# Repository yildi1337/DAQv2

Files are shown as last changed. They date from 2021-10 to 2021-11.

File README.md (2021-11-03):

# DAQv2
A Dual-Channel, 24-Bit, 256 kS/s Real-Time Hi-Speed USB 2.0 Data Acquisition (DAQ) Device based on STM32H7

# Details
The recording of analog measurement signals is often done with so-called data acquisition (DAQ) devices. Commercial devices from [National Instruments](http://www.ni.com) are commonly used, but unfortunately also very expensive. The goal of this project was to develop a first prototype of a low-cost DAQ device that can compete with commercial devices, i.e. both the hardware DAQ board as well as software for receiving and analyzing the data is necessary.

The basic structure of a DAQ is very simple. In principle, only an analog-to-digital converter (ADC) and an FPGA or microcontroller are needed in order to send the measurement data in real time to a computer. Here, the [AD7768-4 from Analog Devices](https://www.analog.com/en/products/ad7768-4.html) has been chosen, which offers up to 4 synchronous channels (but I only use 2 channels), a sampling rate of 256 kS/s and a resolution of 24 bit. Each sample consists of 3 data bytes and one status byte. So with the two channels used, the net data rate is 2 x 256 kS/s x 4 byte = 2.048 MByte/s = 16.384 MBit/s.

To keep the hardware cheap and the compatibility high, I decided to use a microcontroller (and not an FPGA) and a USB connection. Since the net data rate is higher than 12 MBit/s (USB Full-Speed), a USB Hi-Speed connection (up to 480 MBit/s) is required. However, most microcontrollers allow USB Hi-Speed connections only with an additional external PHY. Therefore, in my recent project [DAQv1](https://github.com/yildi1337/DAQv1), I have chosen a microcontroller from Microchip's PIC32MZ family, since they already have the Hi-Speed PHY integrated. Due to the poor documentation of the Microchip microcontrollers, I decided to use a microcontroller from the STM32H7 family again, which can be easily operated with an external PHY.

Technical summary of the developed platform:
* ADC: [AD7768-4BSTZ](https://www.analog.com/en/products/ad7768-4.html)
* Number of channels: 2
* Sample rate: 256 kS/s
* Resolution: 24 bit
* Reference voltage: 5 V
* Microcontroller: [STM32H753ZIT6](https://www.st.com/en/microcontrollers-microprocessors/stm32h753zi.html)
* USB 2.0 Hi-Speed (net data rate: 16.384 MBit/s)
* Preamlifier: 0-80 dB by means of two [AD8338ACPZ-R7](https://www.analog.com/en/products/ad8338.html)
* Programmable input coupling (AC with lower cutoff frequency of approx. 10 mHz and DC)
* Programmable input type (single ended and differential)
* LC Display for displaying input configuration
* Two buttons for chaning the input configuration
* Noise: See below

If you have any questions, feel free to contact me!

# Pictures

Not yet available.

# 3D Model

A 3D model of the PCB can be found in the Autodesk Fusion Cloud where it can be downloaded in various file types.

<p align="center">
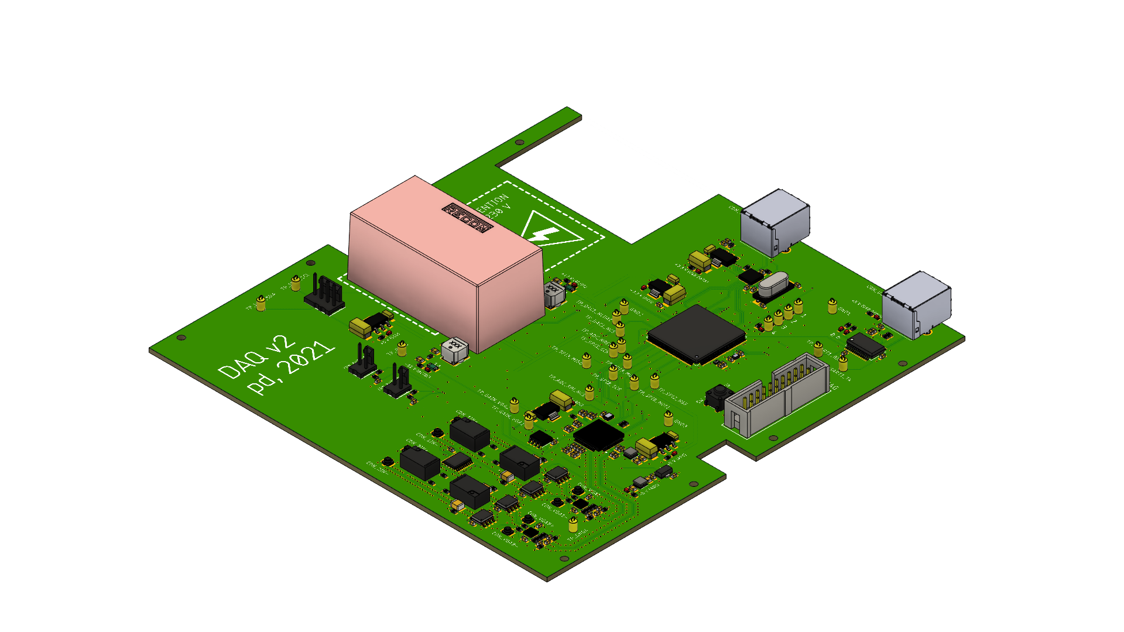
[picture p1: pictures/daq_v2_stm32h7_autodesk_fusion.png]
    
</p>

In addition, a step file of the complete device, i.e. a model of the PCB embedded into the housing ([TEKO 935.9](https://www.teko.it/de/produkte/produktfamilie/FP/serie/euro-93)), can be found in the directory *3d_model*.

<p align="center">
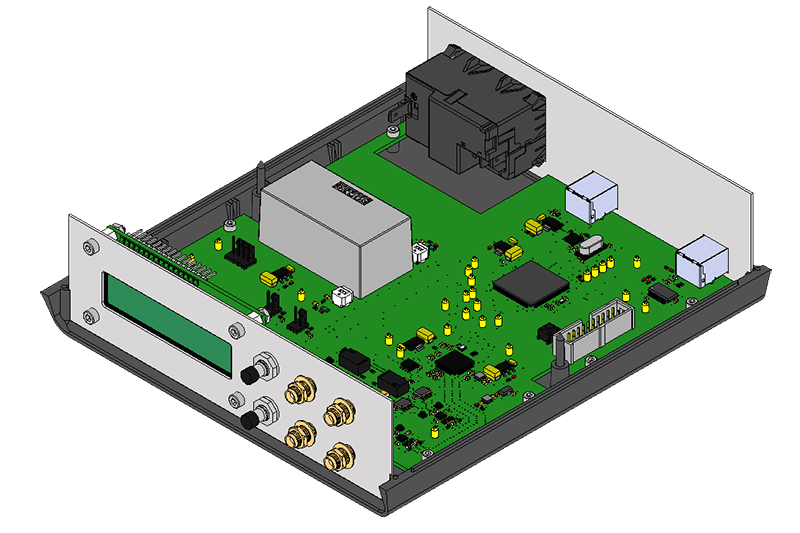
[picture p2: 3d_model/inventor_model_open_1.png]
  
</p>

<p align="center">
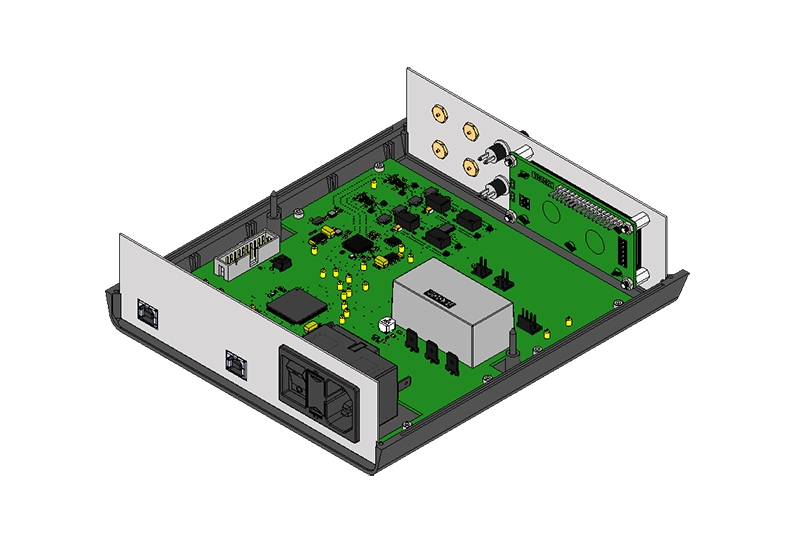
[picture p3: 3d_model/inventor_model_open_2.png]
  
</p>

<p align="center">
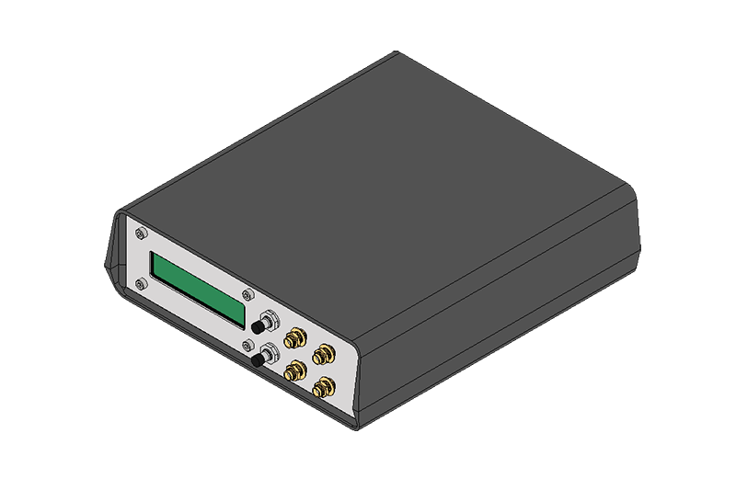
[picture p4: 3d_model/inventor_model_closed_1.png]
  
</p>

<p align="center">
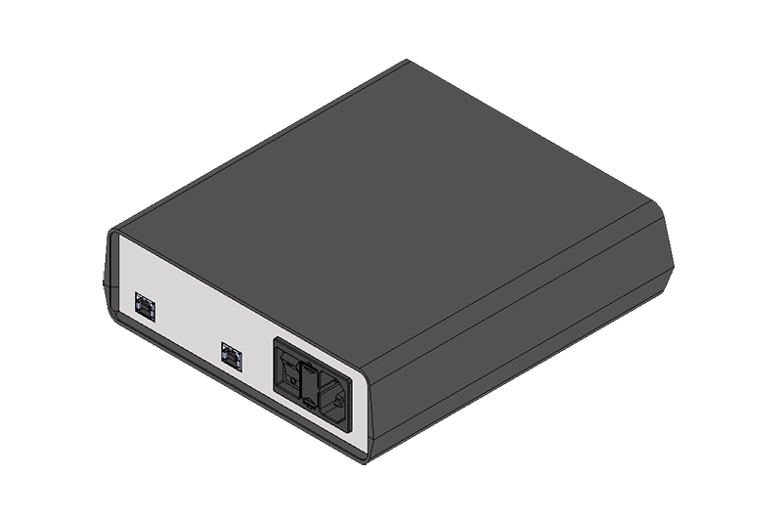
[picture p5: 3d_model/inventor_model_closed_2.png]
  
</p>

# Schematics
Please see subdirectory *schematics*.

# Board
The PCB was designed in Autodesk EAGLE 9.6.2 and manufactured by [JLCPCB](https://jlcpcb.com/). All Gerber files can be found in the subdirectory *gerber_files*.

<p align="center">
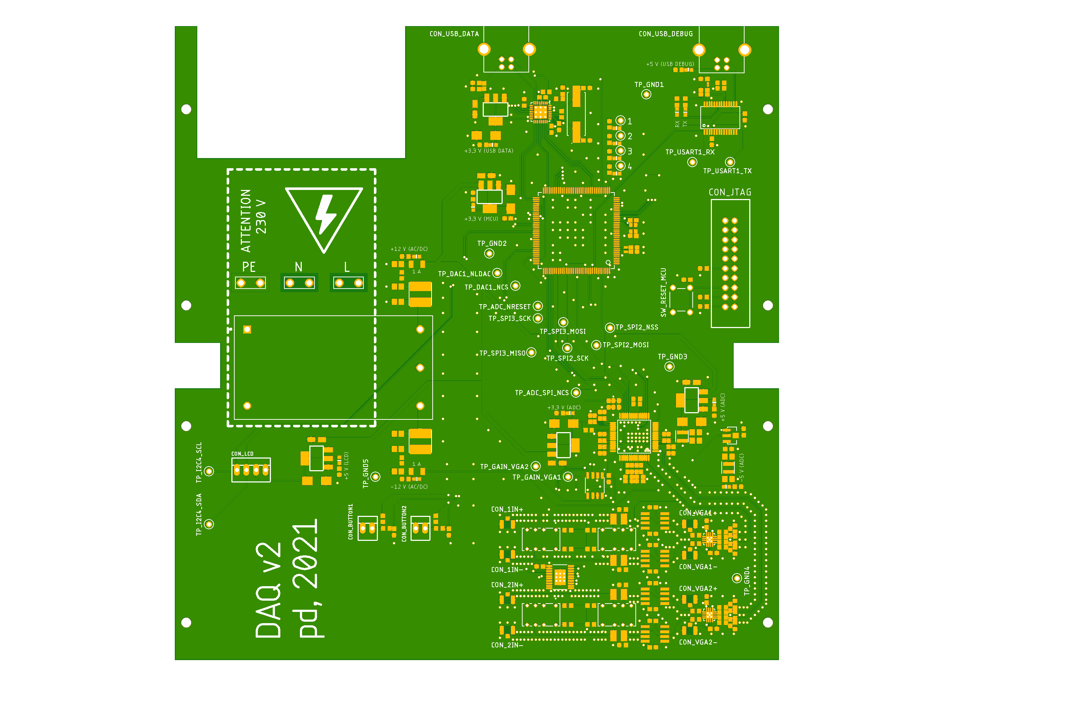
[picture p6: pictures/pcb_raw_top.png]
  
</p>

<p align="center">
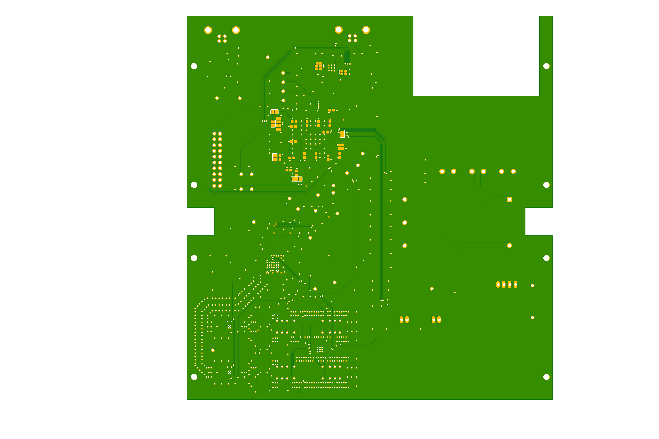
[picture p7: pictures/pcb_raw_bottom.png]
  
</p>

# Firmware
The source code of software running on the STM32H753ZIT6 can be found in the subdirectory *firmware*). For the development and debugging I used STM32CubeIDE version 1.7.0. For programming I used the ST-LINK/V2 in-circuit debugger/programmer.

# USB Debug Interface

A tool for the graphical display of status information and for controlling the DAQ v2 hardware via the virtual serial interface (second USB-B port) has been developed in Python, see subdirectory *debug_interface*.

<p align="center">
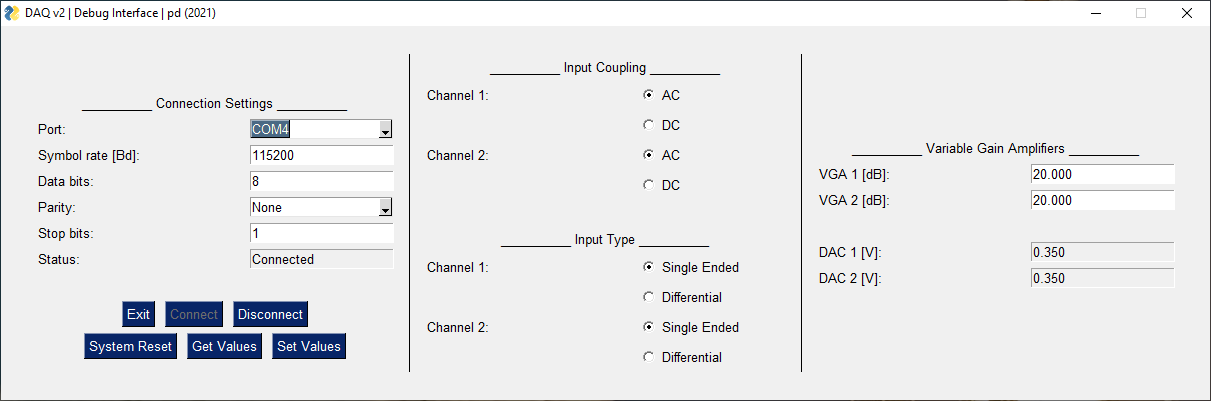
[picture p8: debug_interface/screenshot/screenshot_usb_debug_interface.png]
  
</p>

# LabVIEW Real-Time Data Receiver

A software vor real-time data reception and visualization of the signals both in time and frequency domain has been developed in LabVIEW, see subdirectory *labview*.

<p align="center">
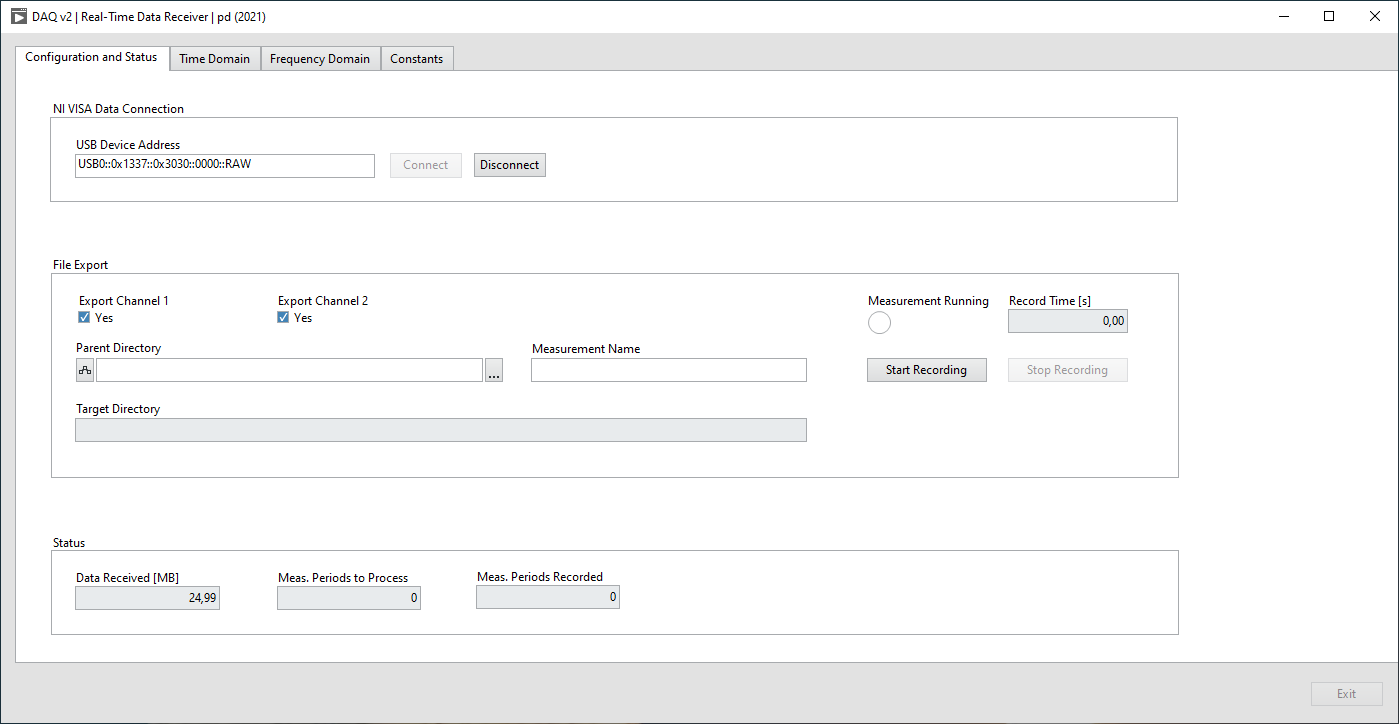
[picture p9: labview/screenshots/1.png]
  
</p>

<p align="center">
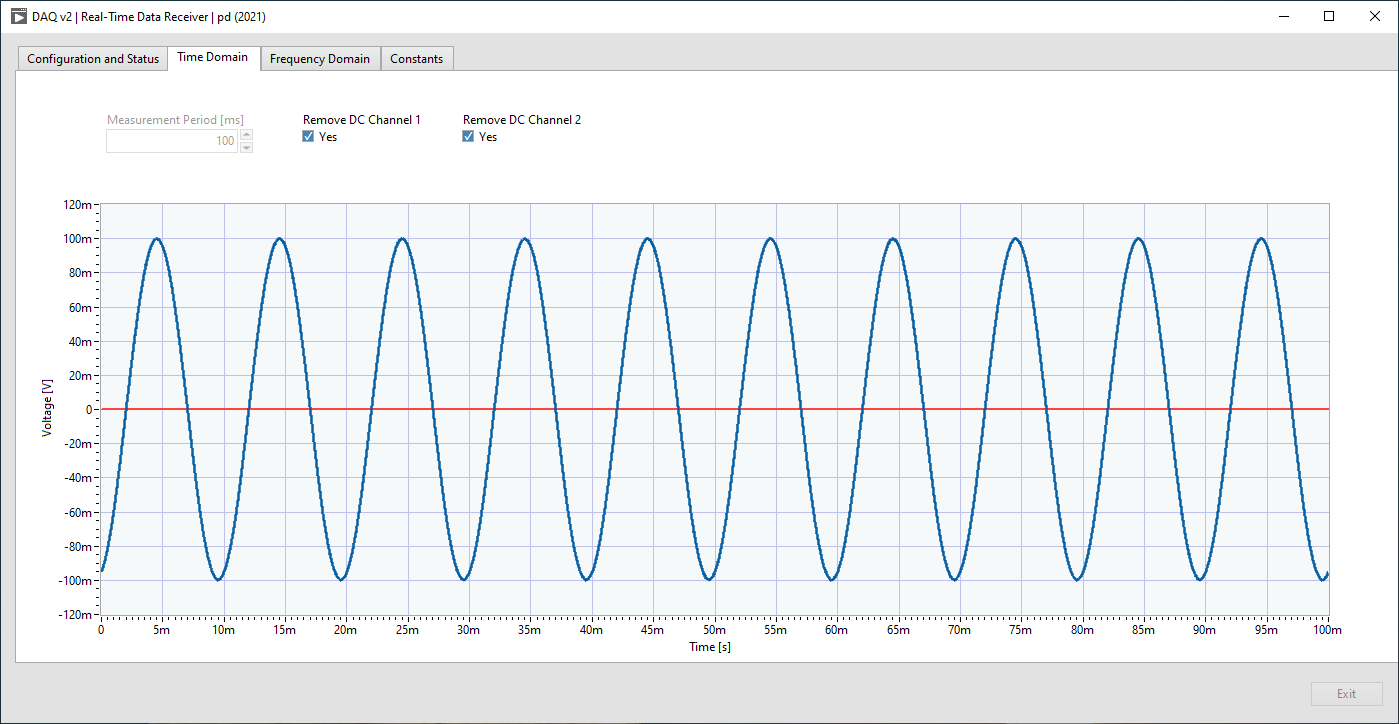
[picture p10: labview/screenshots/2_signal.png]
  
</p>

<p align="center">
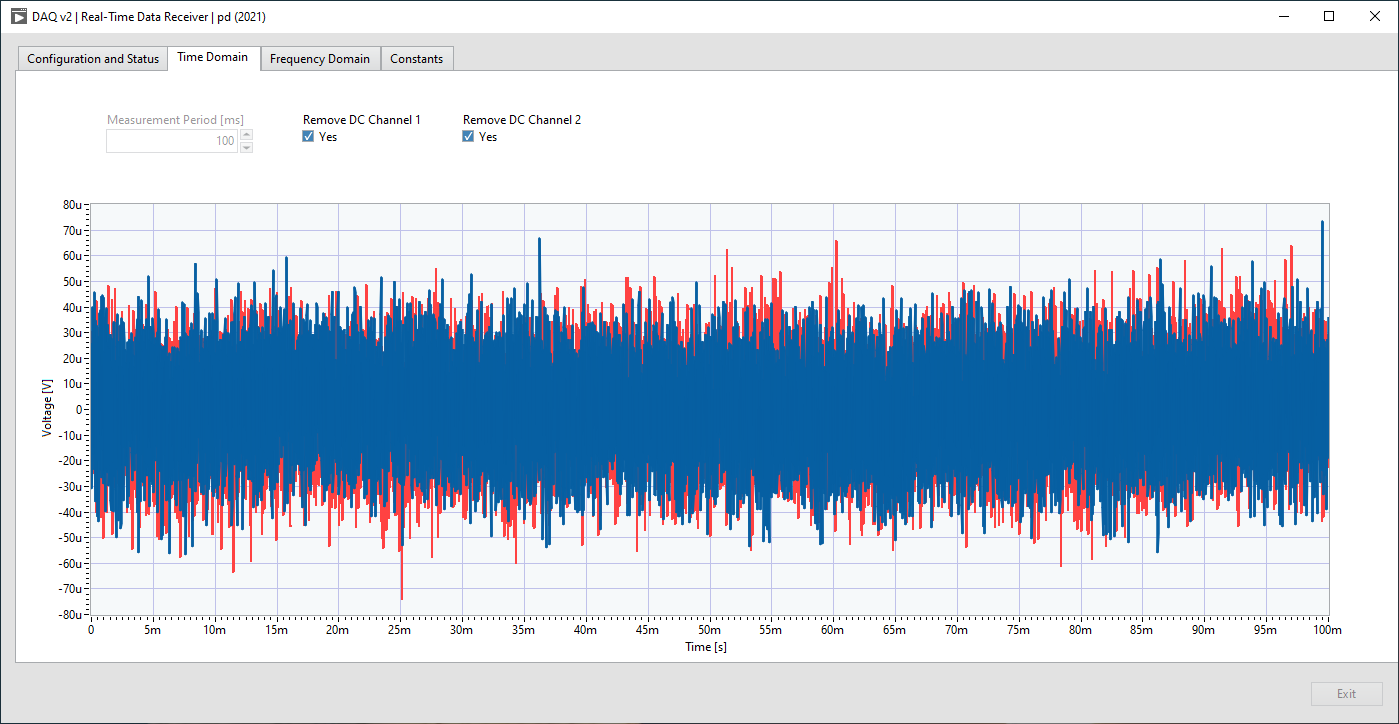
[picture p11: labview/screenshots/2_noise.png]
  
</p>

<p align="center">
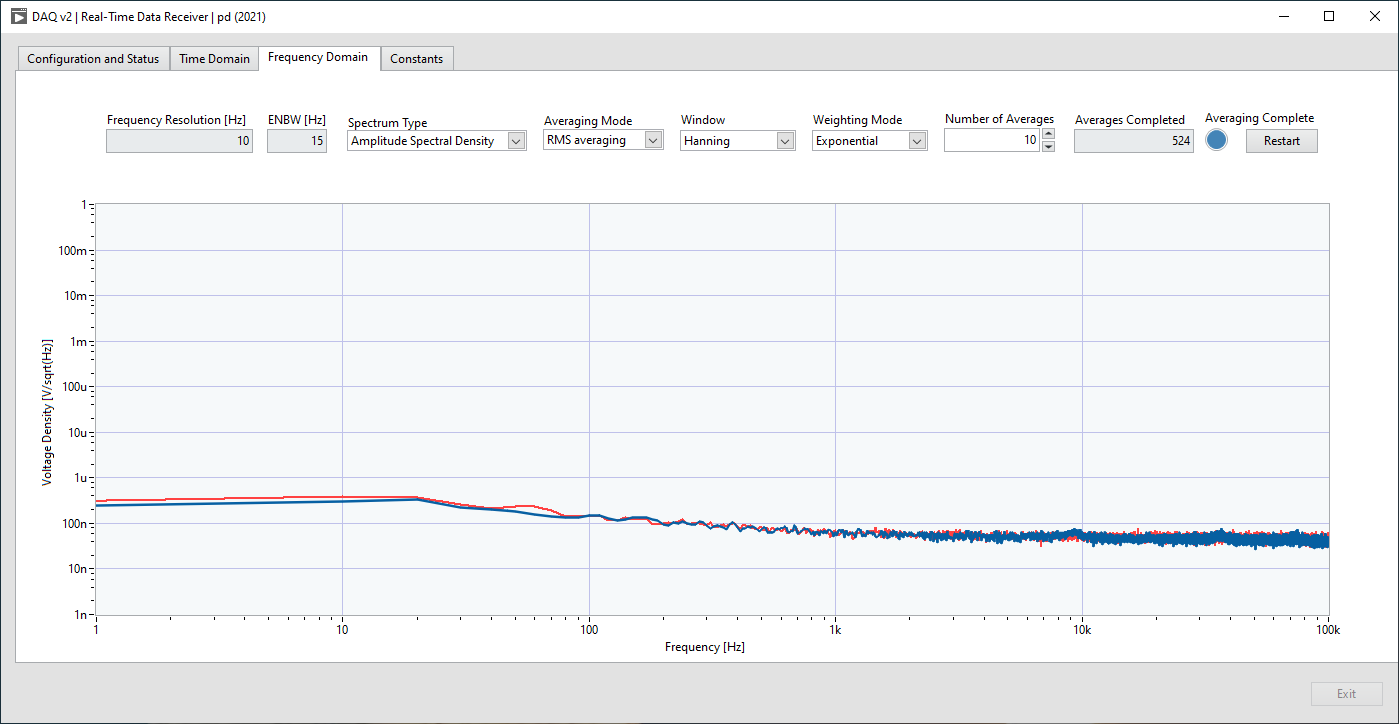
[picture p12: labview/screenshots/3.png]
  
</p>

<p align="center">
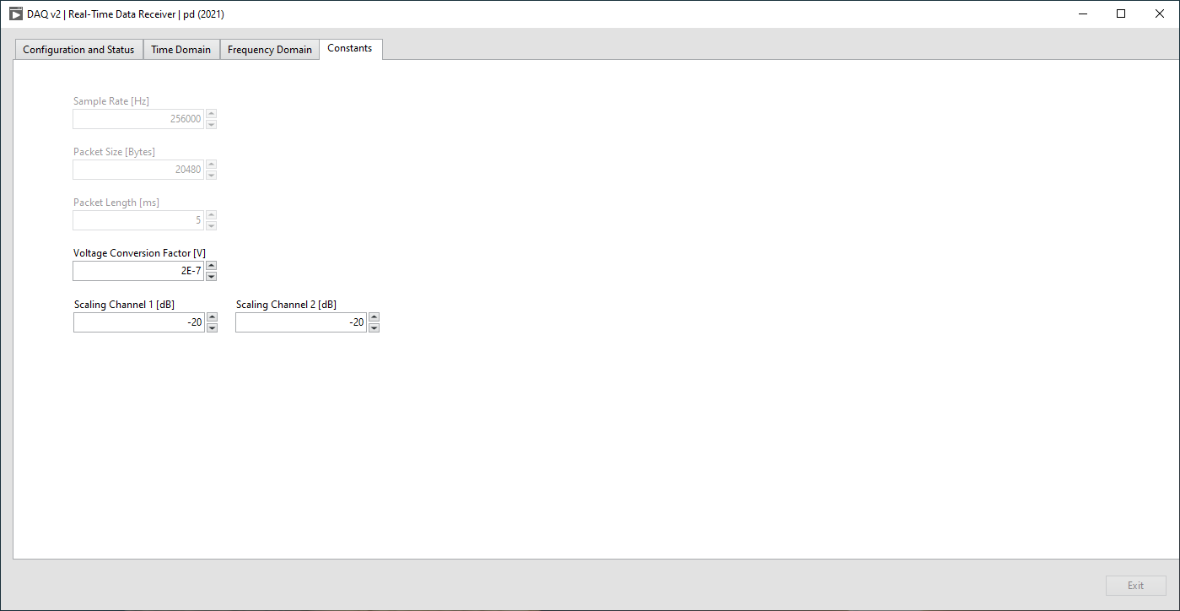
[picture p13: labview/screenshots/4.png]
  
</p>

# Noise

The voltage noise densities were measured for various cases (open inputs, shortened inputs, and 50 Ohm resistors connected to the inputs). 

Not yet available.

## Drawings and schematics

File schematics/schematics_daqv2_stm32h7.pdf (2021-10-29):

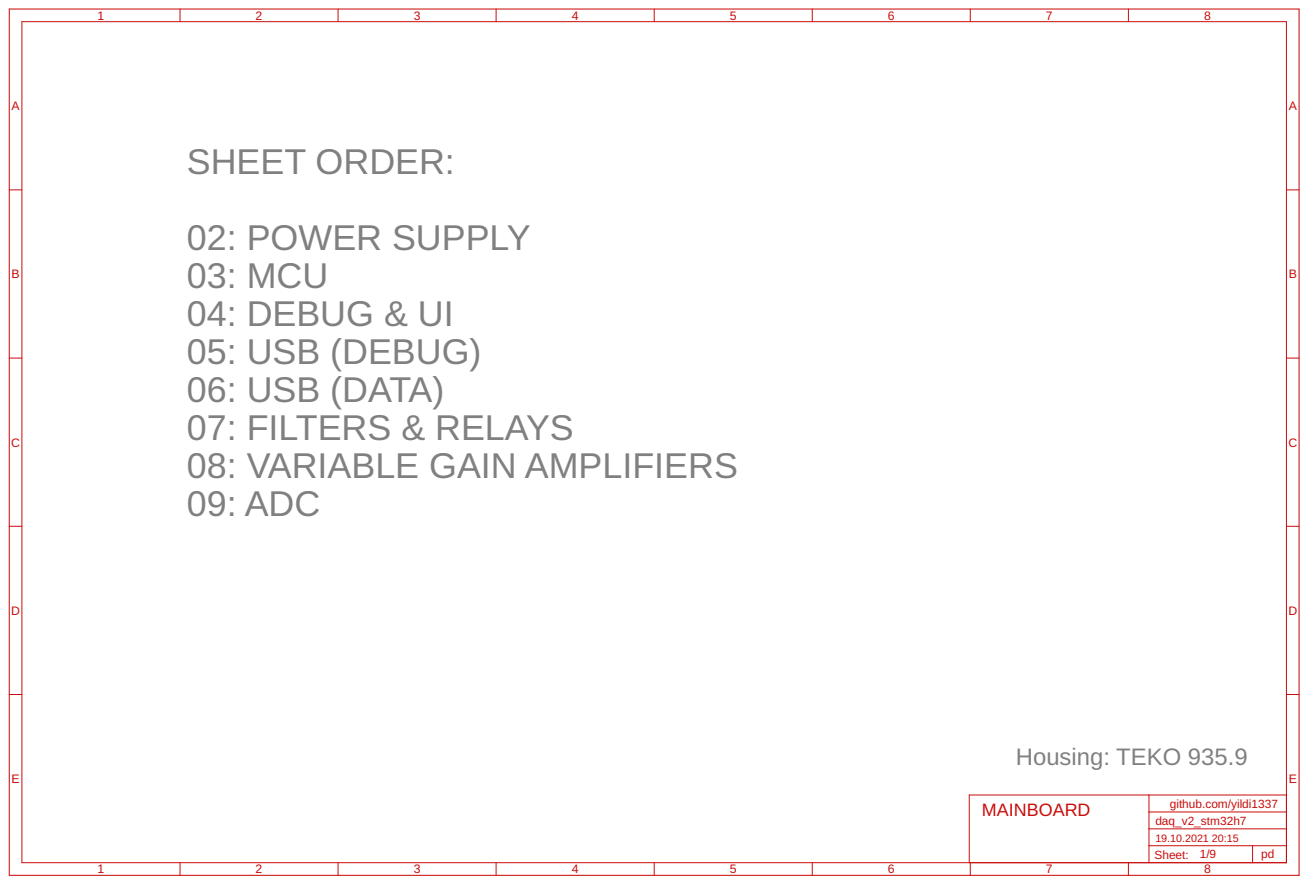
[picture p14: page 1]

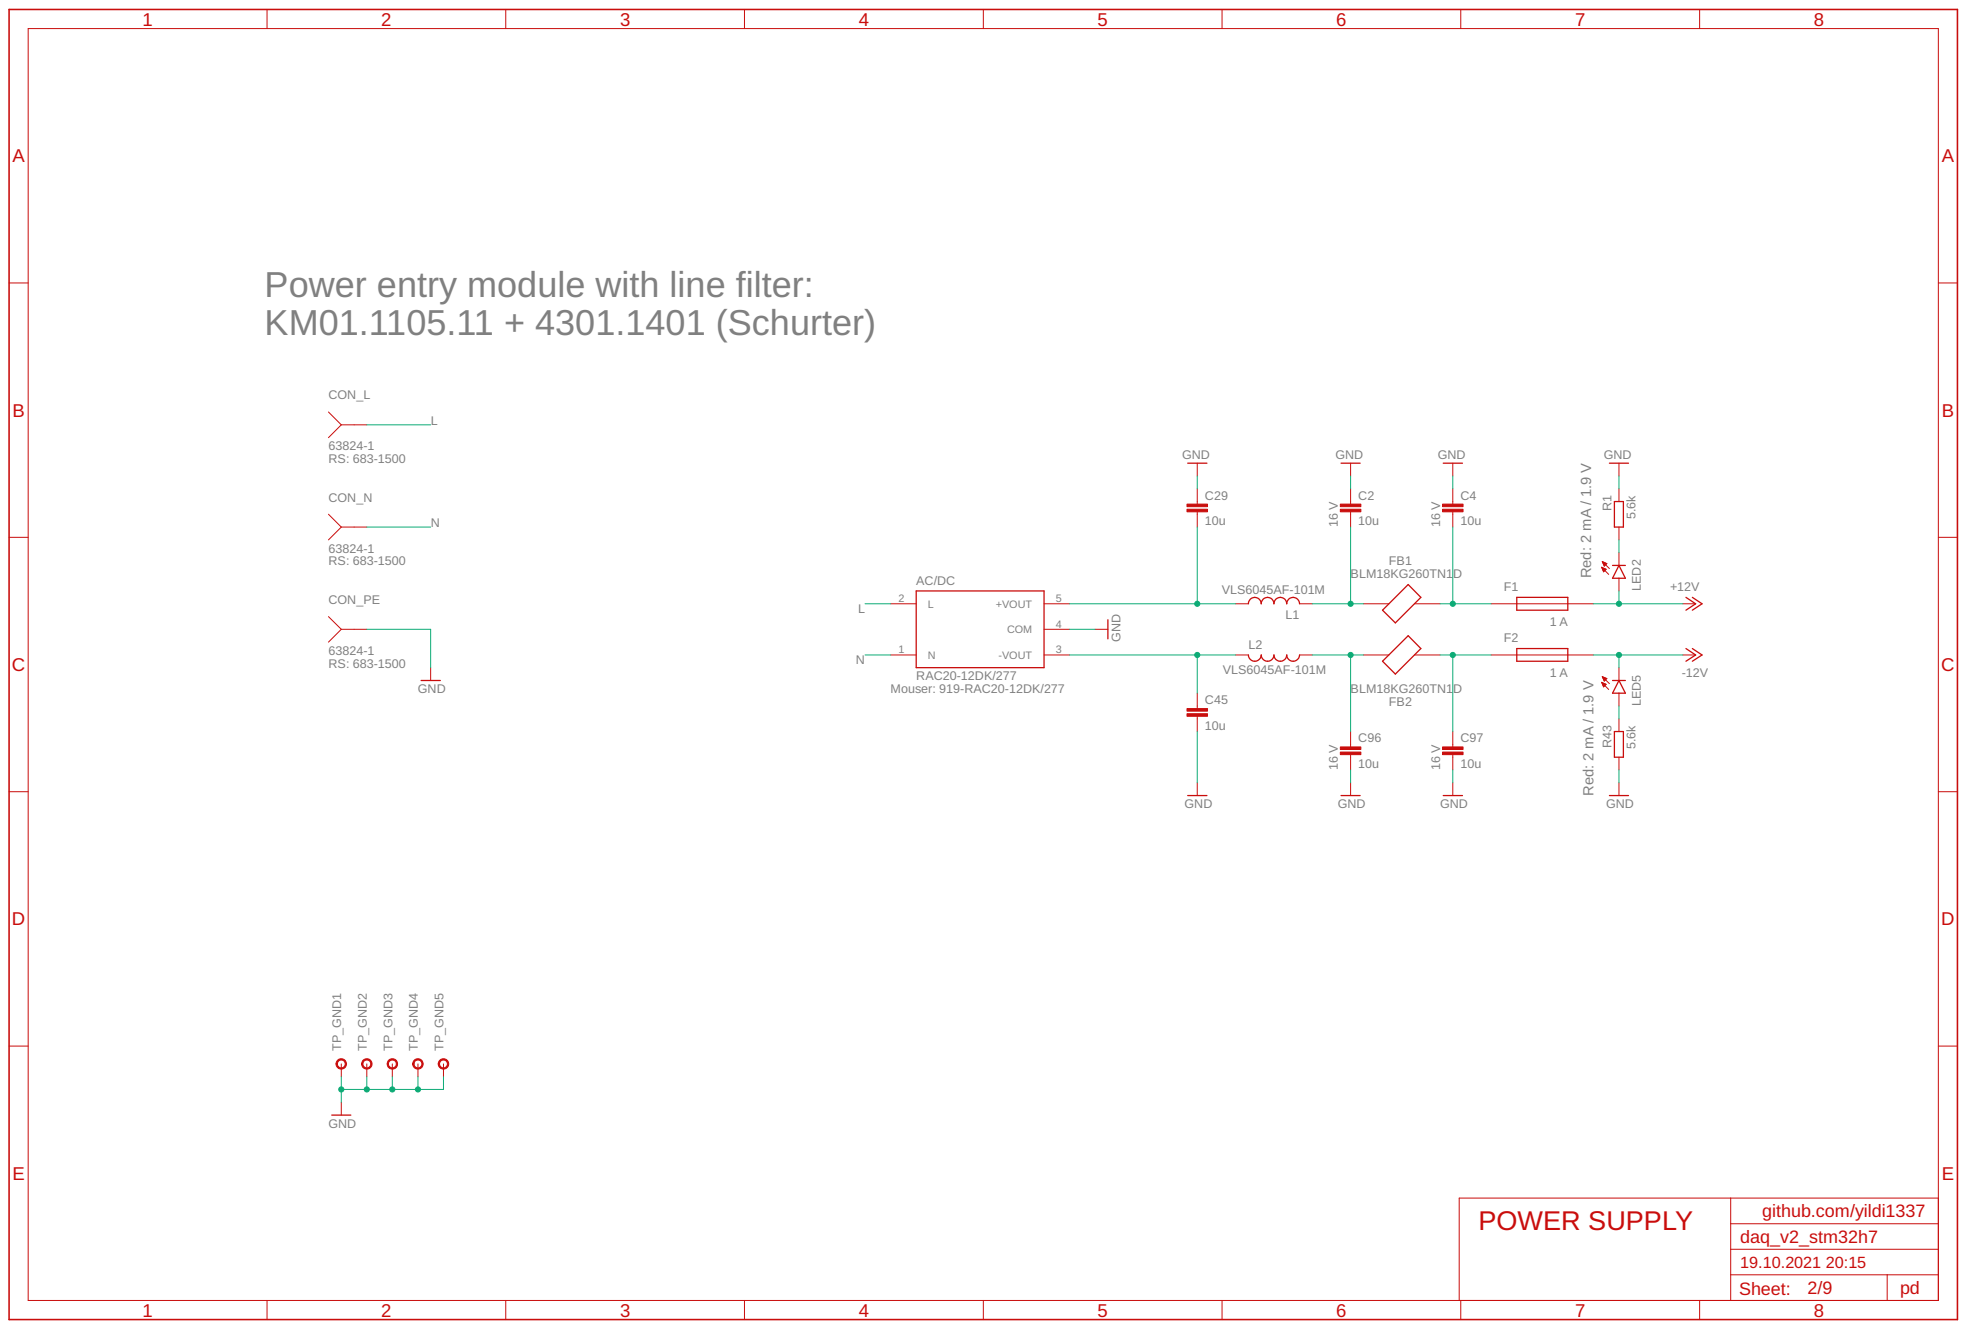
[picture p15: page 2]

Power entry module with line filter:
KM01.1105.11 + 4301.1401 (Schurter)

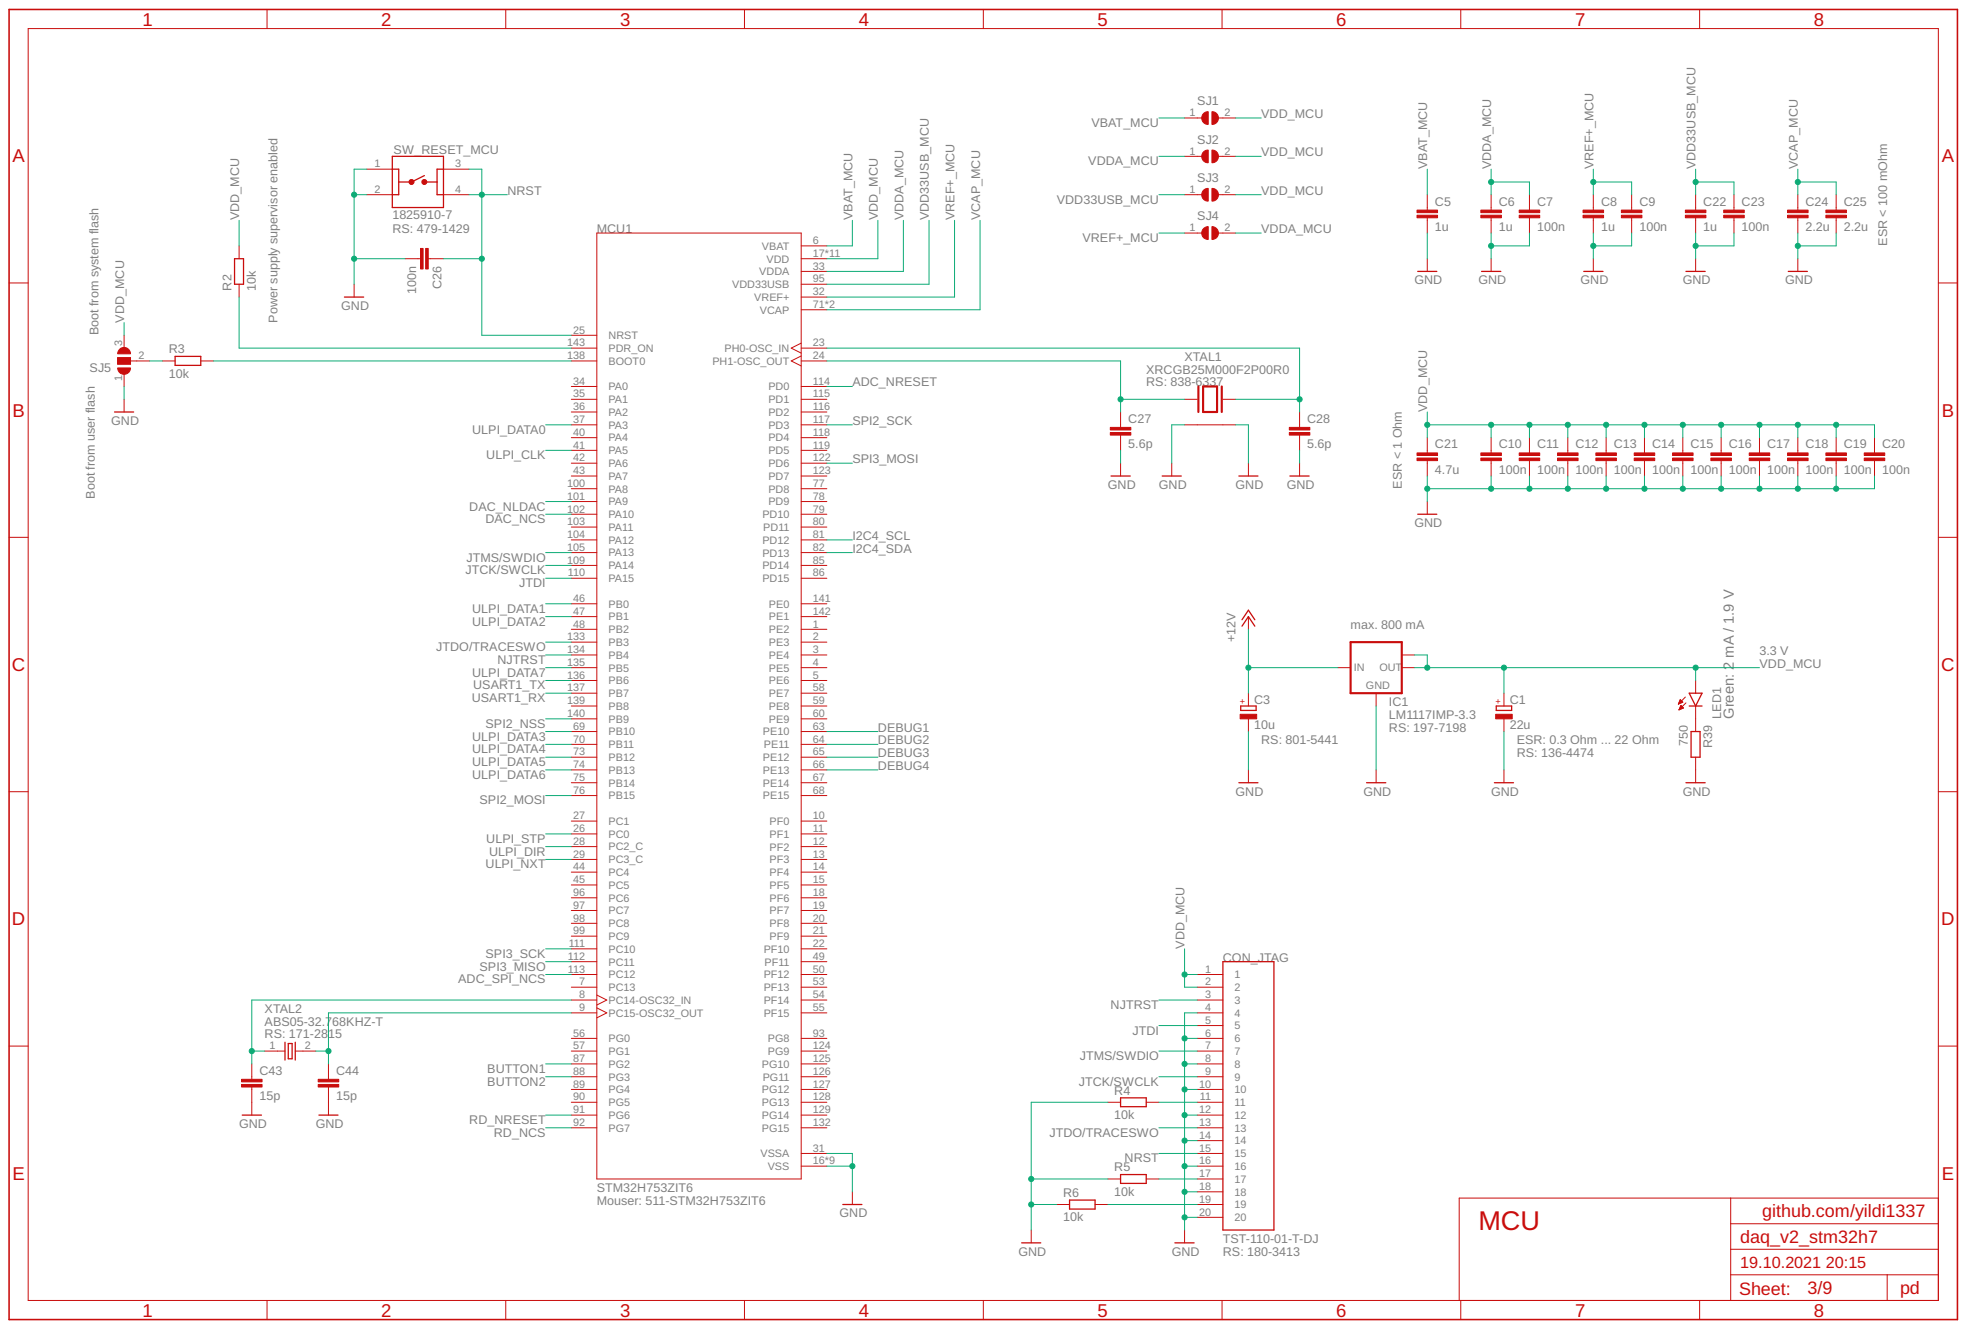
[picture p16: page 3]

Power supply supervisor enabled

Boot from user flash Boot from system flash

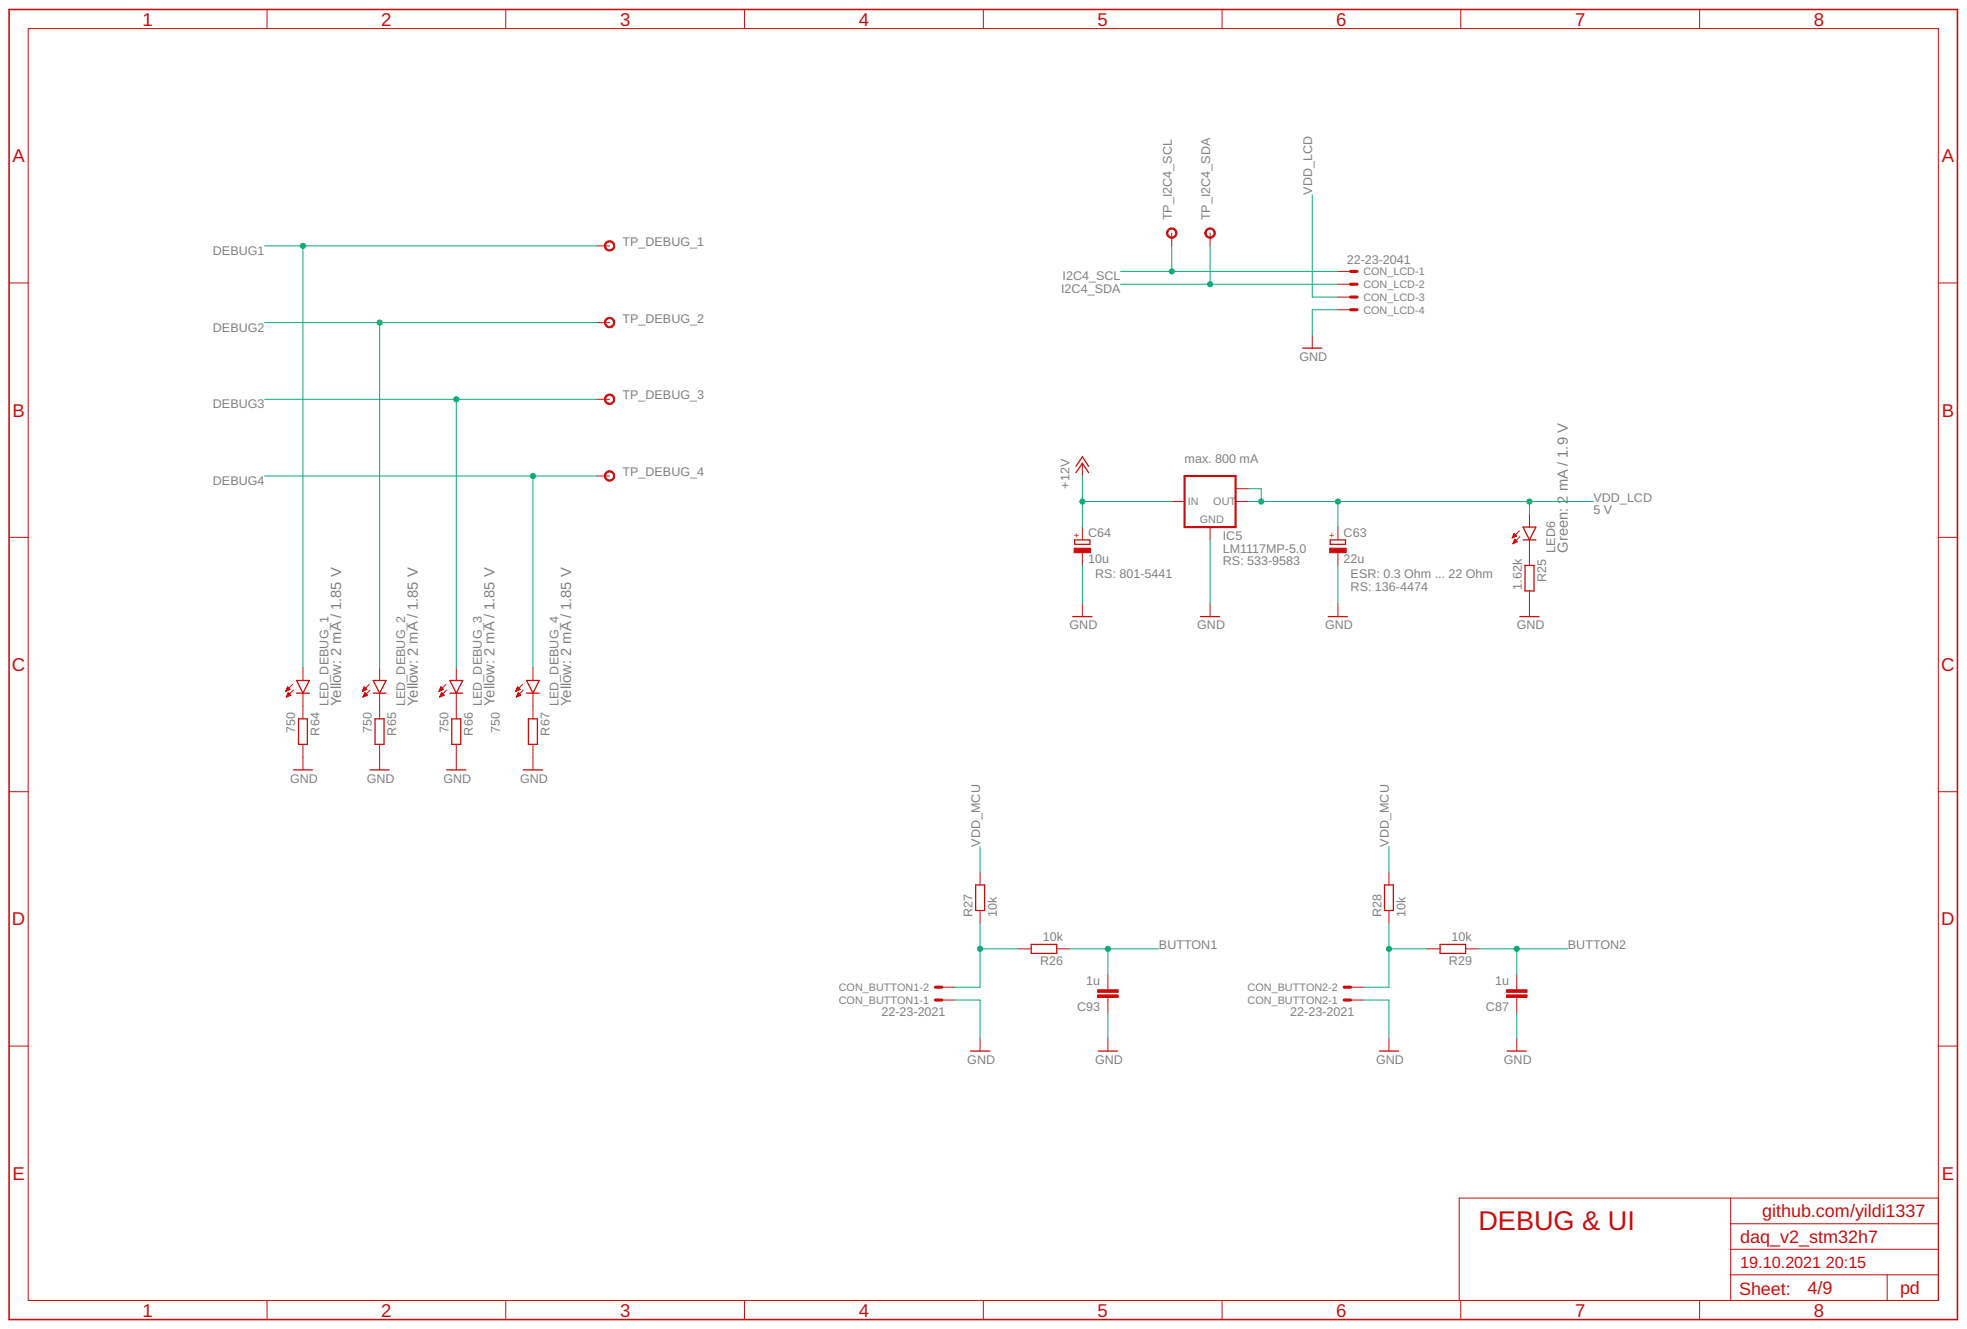
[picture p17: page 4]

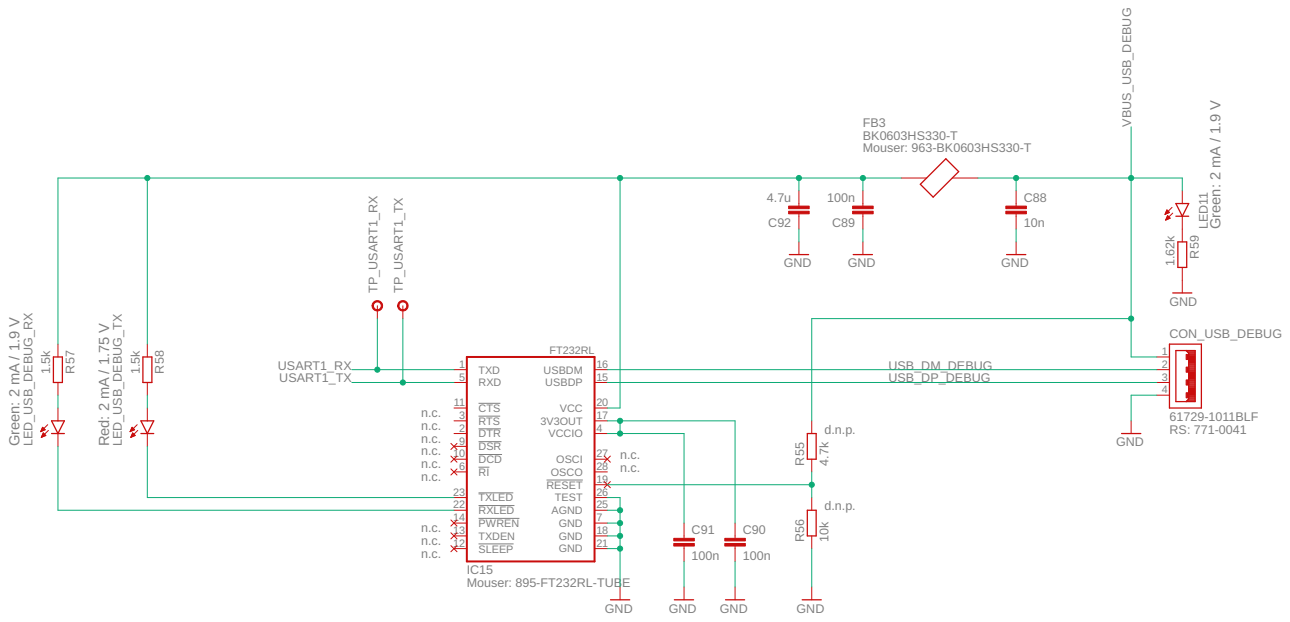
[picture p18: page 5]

15 | USB_DP_DEBUG 3

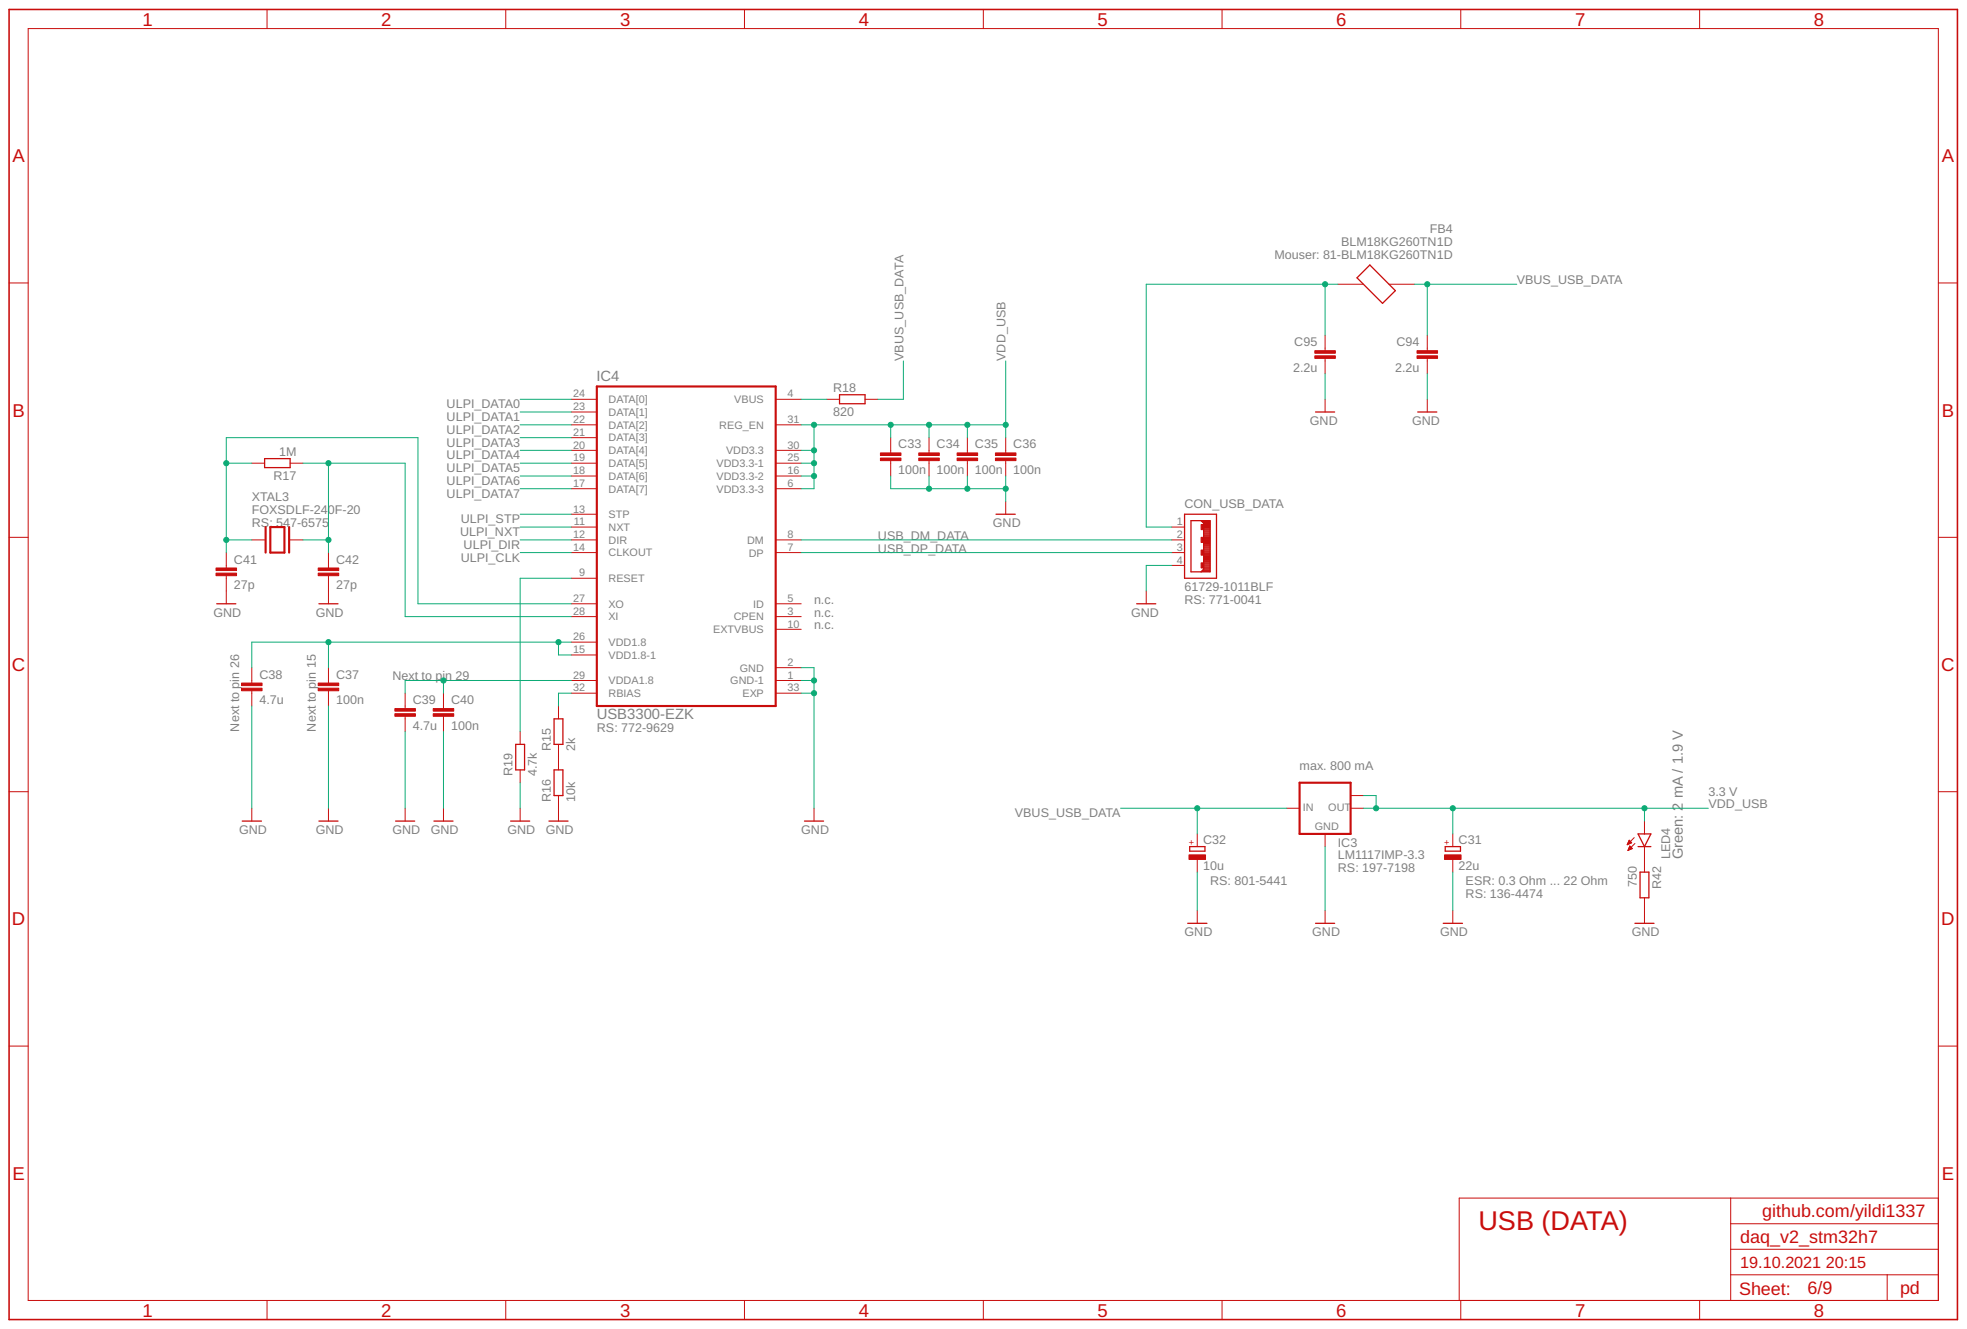
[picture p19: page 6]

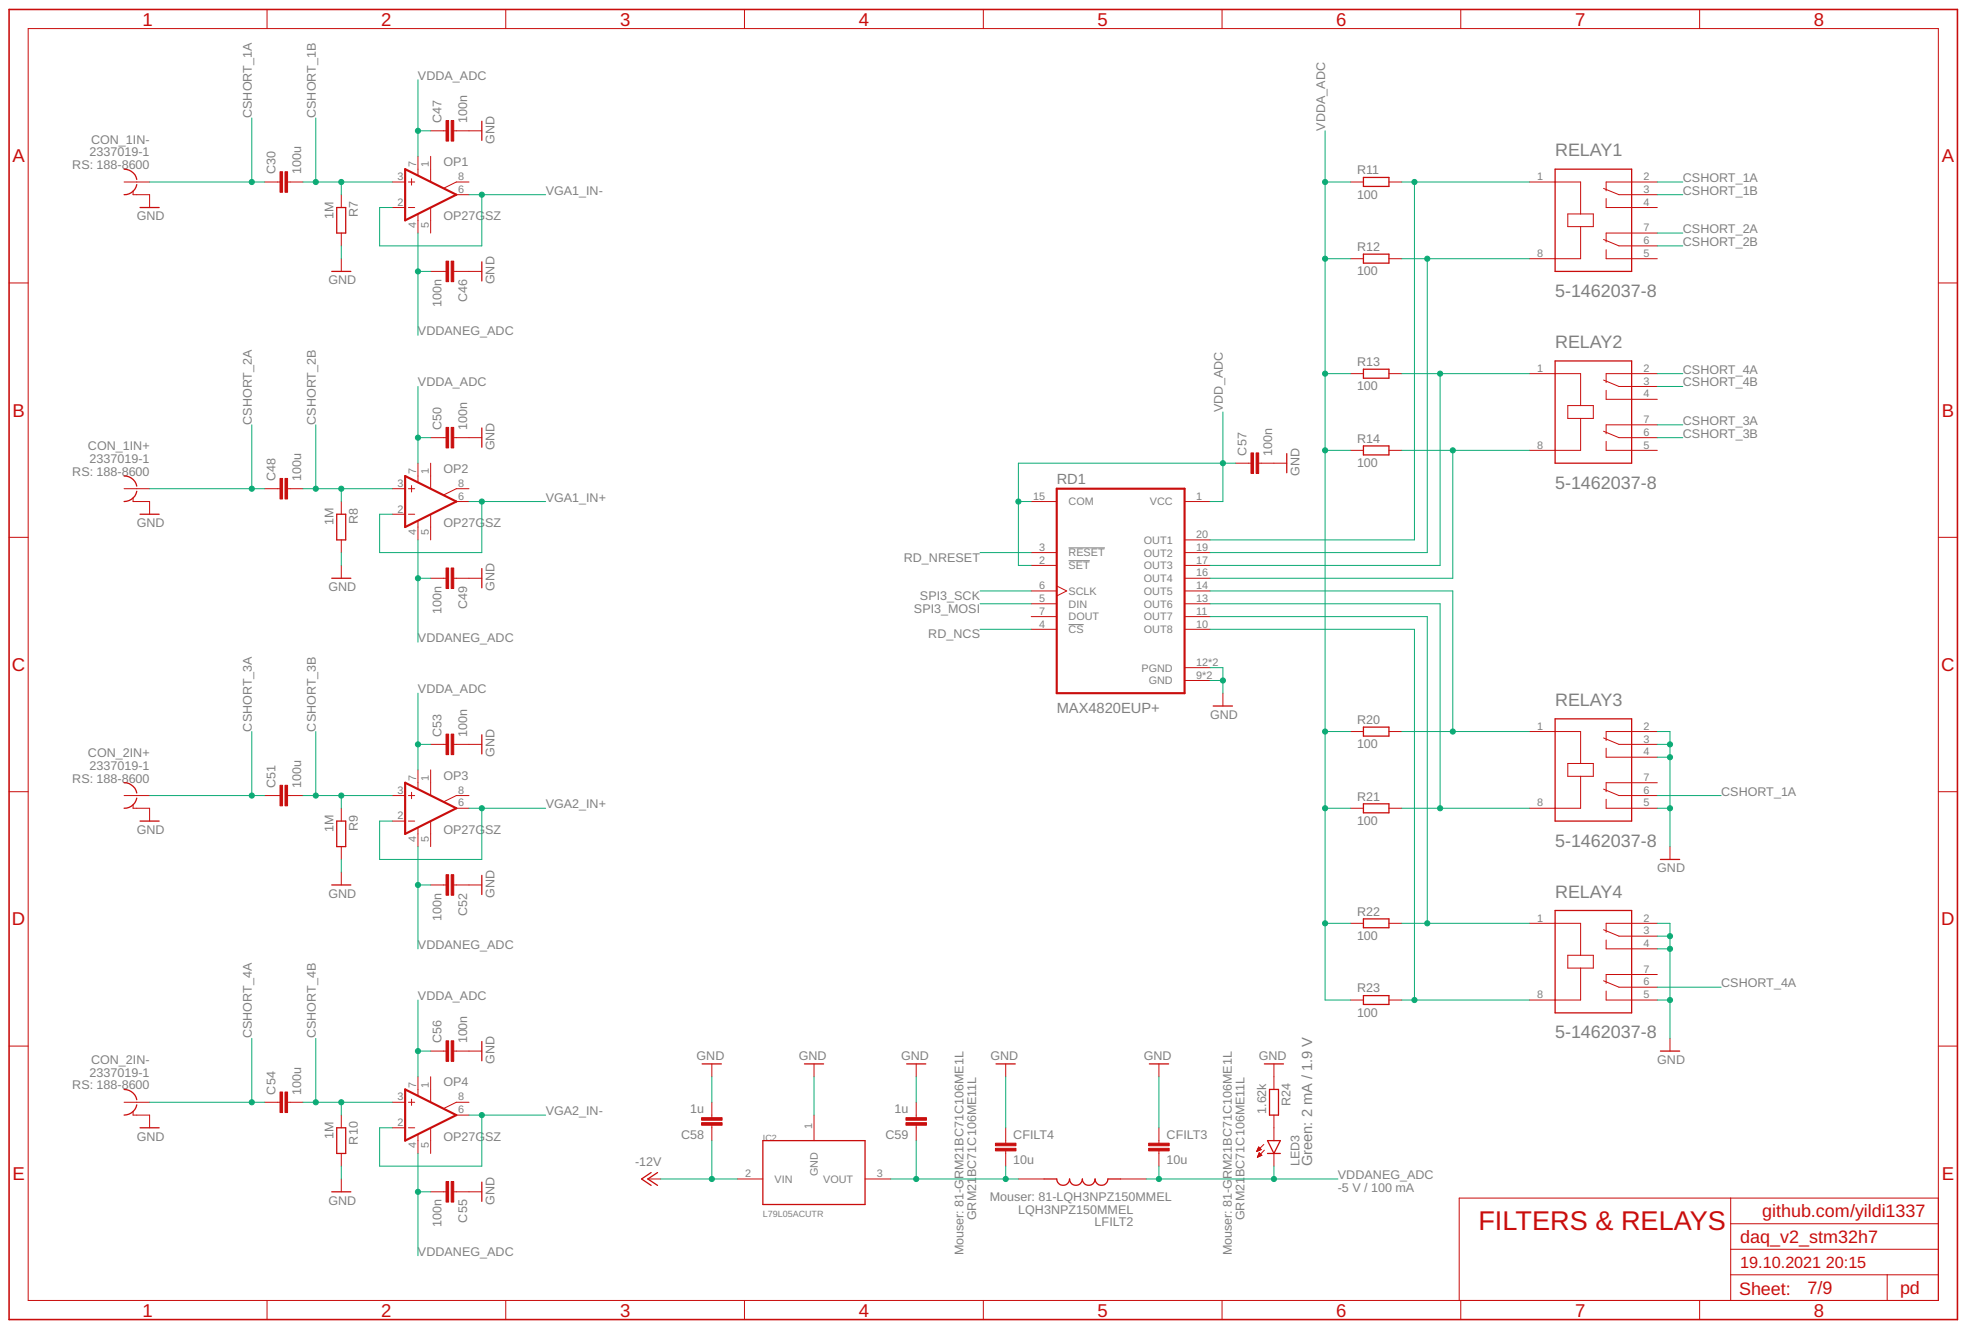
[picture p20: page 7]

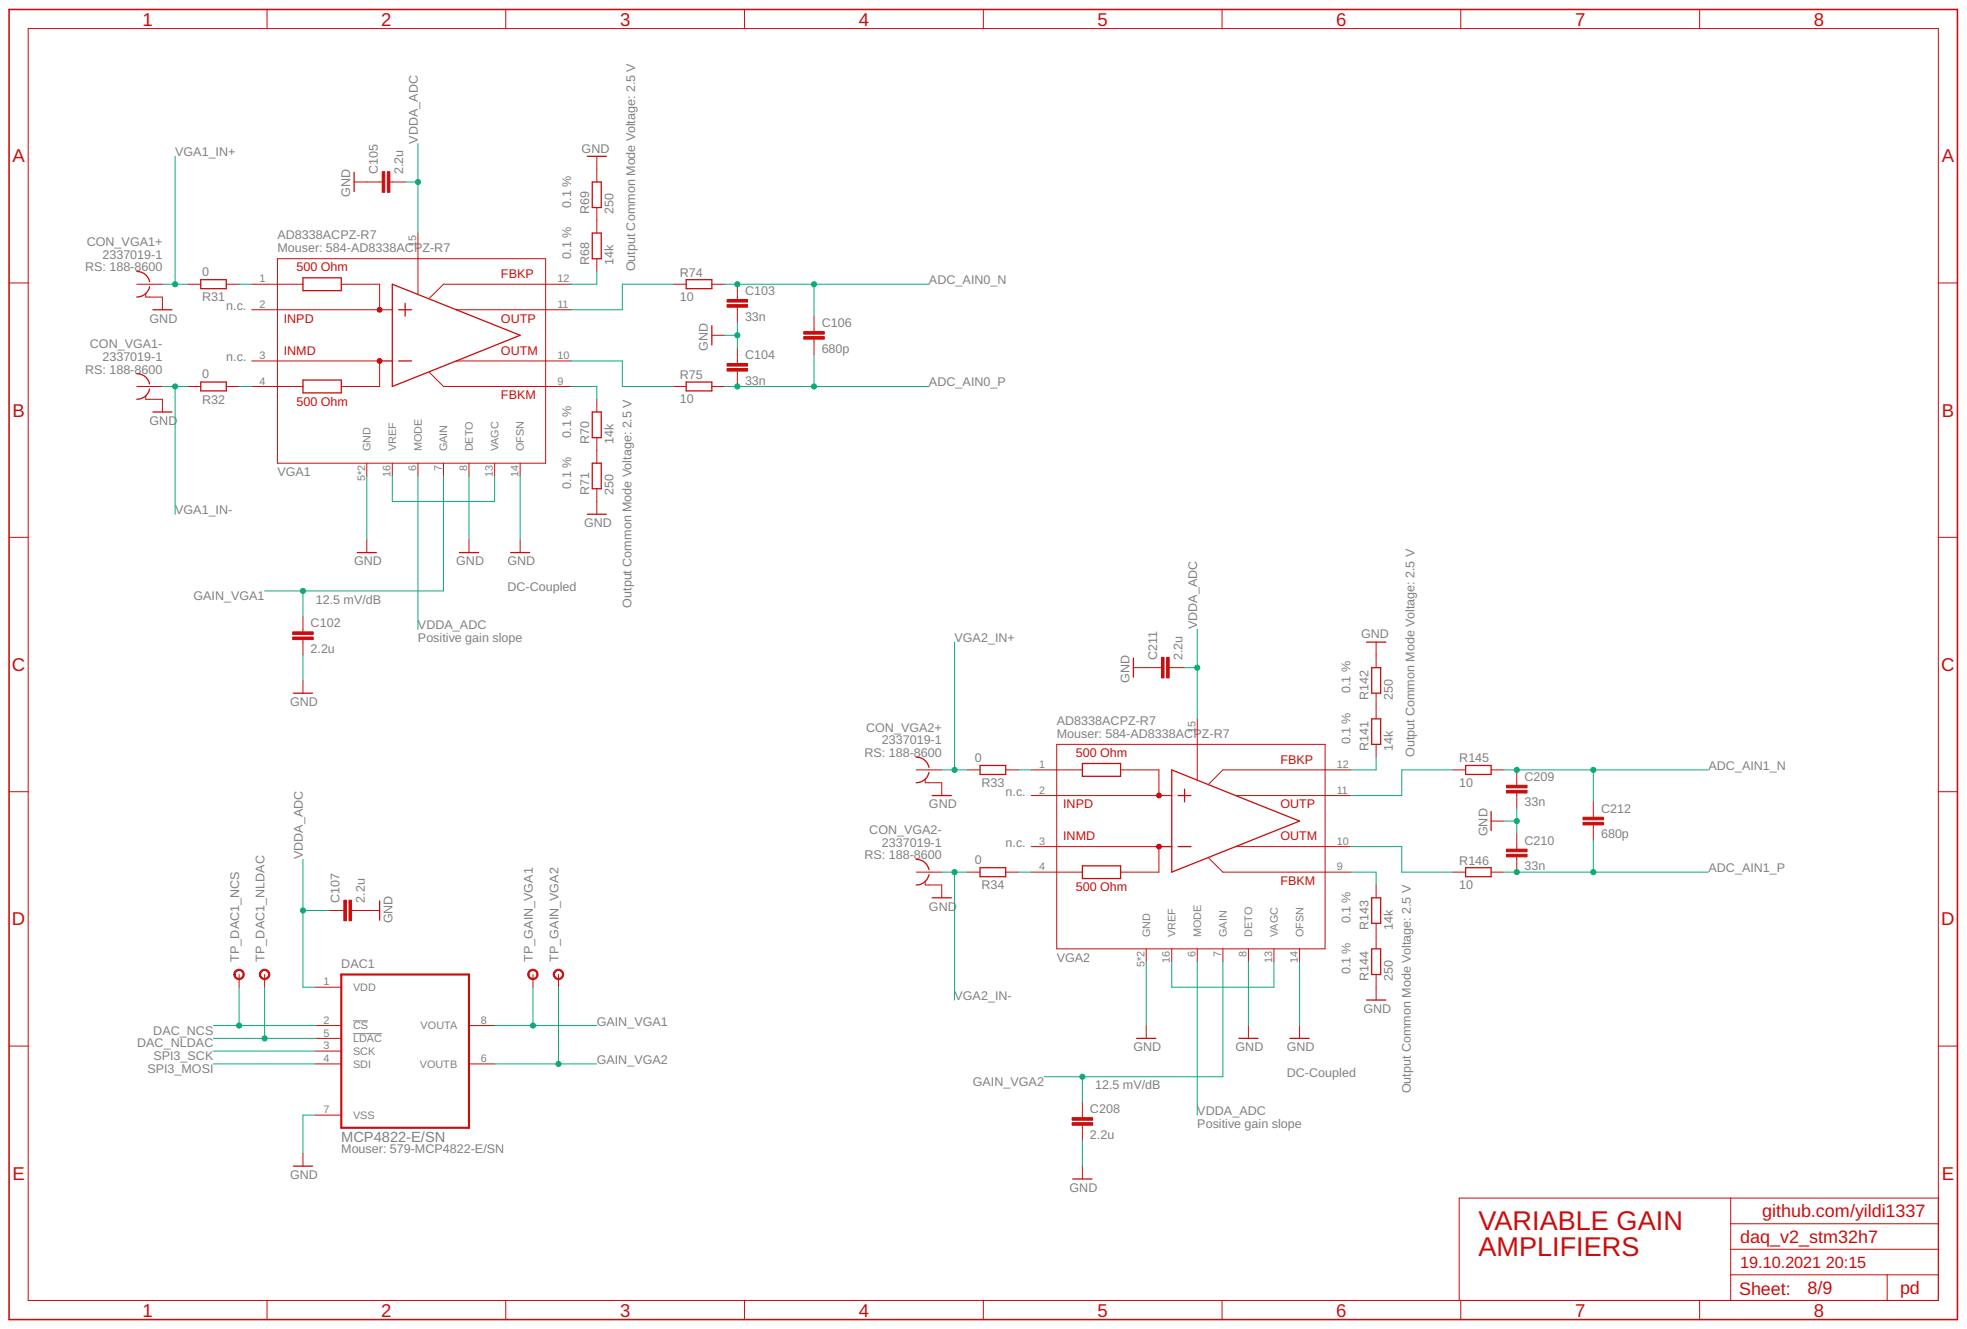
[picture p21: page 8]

Output Common Mode Voltage: 2.5 V

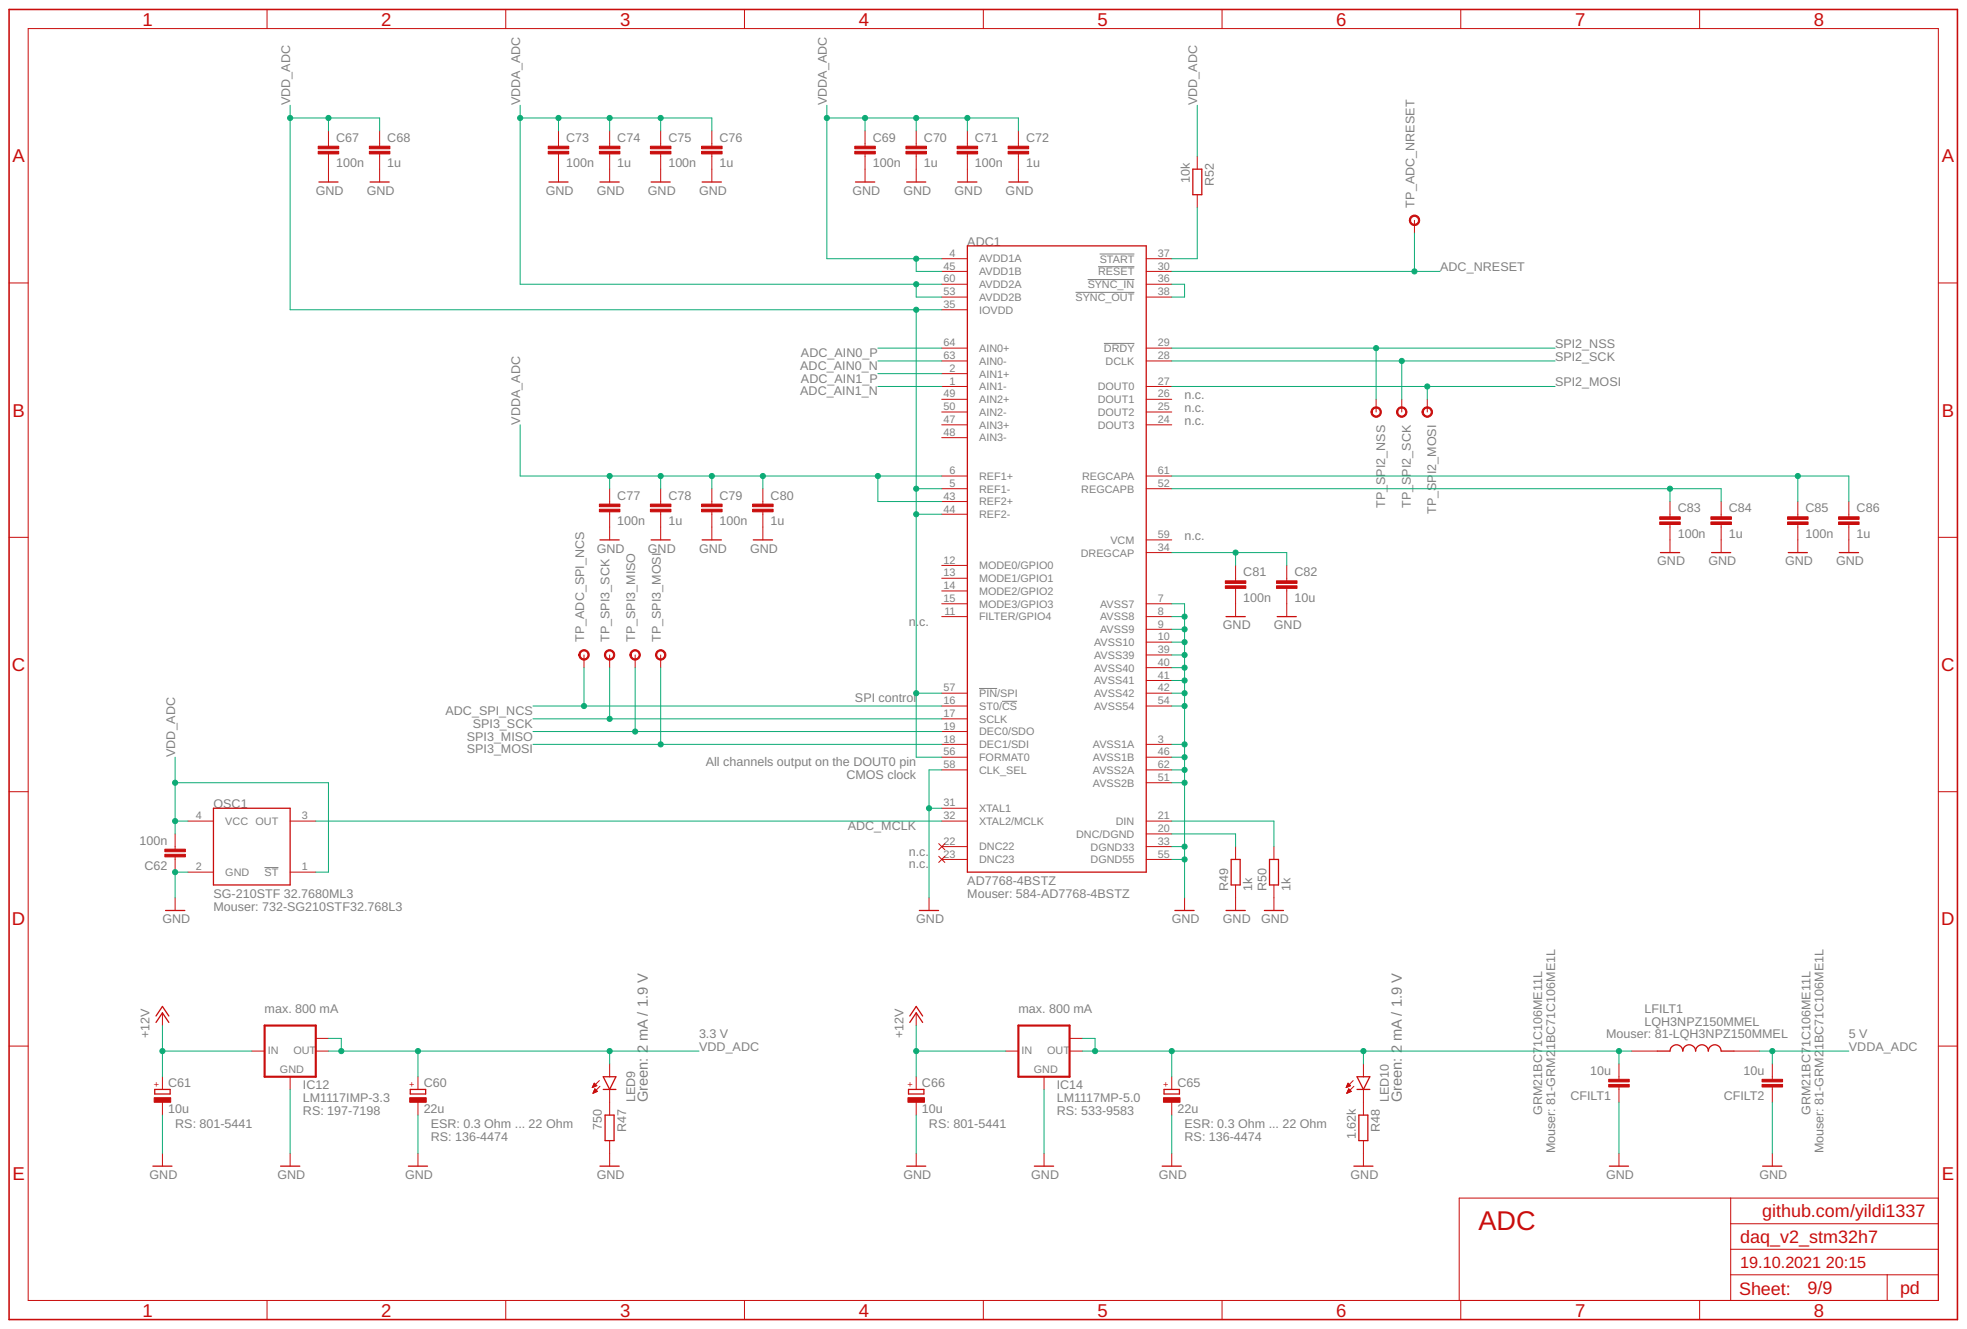
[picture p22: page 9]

All channels output on the DOUT0 pin CMOS clock

3 ST | 21 DGND55 20

33 DNC/DGND

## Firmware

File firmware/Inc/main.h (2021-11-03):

/*
 *******************************************************************************
 * File:            main.h
 * Date:            2020-11-02
 * Author:          Phillip Durdaut
 * Summary:         Main include file with main program definitions
 * Notes:           -
 *******************************************************************************
 */

/* Define to prevent recursive inclusion -------------------------------------*/
#ifndef __MAIN_H
#define __MAIN_H

/* Includes ------------------------------------------------------------------*/
#include <stdio.h>
#include <stdlib.h>
#include <string.h>
#include <stdbool.h>
#include <stdint.h>
#include <float.h>
#include <ctype.h>

#include "stm32h7xx.h"
#include "stm32h7xx_hal.h"
#include "stm32h7xx_it.h"

/* Public defines ------------------------------------------------------------*/

/* ADC */
#define MAIN_ADC_SAMPLES_PER_SECOND                     256e3
#define MAIN_ADC_SAMPLES_PER_MILLI_SECOND               256
#define MAIN_ADC_NUM_CHANNELS                           4
#define MAIN_ADC_BYTES_PER_SAMPLE_PER_CHANNEL           4
#define MAIN_ADC_BYTES_PER_SAMPLE                       (MAIN_ADC_NUM_CHANNELS * MAIN_ADC_BYTES_PER_SAMPLE_PER_CHANNEL)
#define MAIN_ADC_BYTES_PER_SECOND_PER_CHANNEL           (MAIN_ADC_BYTES_PER_SAMPLE_PER_CHANNEL * MAIN_ADC_SAMPLES_PER_SECOND)
#define MAIN_ADC_BYTES_PER_SECOND                       (MAIN_ADC_NUM_CHANNELS * MAIN_ADC_BYTES_PER_SAMPLE_PER_CHANNEL * MAIN_ADC_SAMPLES_PER_SECOND)
#define MAIN_ADC_BYTES_PER_MILLI_SECOND_PER_CHANNEL     (MAIN_ADC_BYTES_PER_SAMPLE_PER_CHANNEL * MAIN_ADC_SAMPLES_PER_MILLI_SECOND)
#define MAIN_ADC_BYTES_PER_MILLI_SECOND                 (MAIN_ADC_NUM_CHANNELS * MAIN_ADC_BYTES_PER_SAMPLE_PER_CHANNEL * MAIN_ADC_SAMPLES_PER_MILLI_SECOND)

/* USB */
#define MAIN_USB_VENDOR_ID                              0x1337
#define MAIN_USB_PRODUCT_ID                             0x3030
#define MAIN_USB_LANG_ID_STRING_US                      0x0409
#define MAIN_USB_LANG_ID_STRING_DE                      0x0407
#define MAIN_USB_LANG_ID_STRING                         MAIN_USB_LANG_ID_STRING_US
#define MAIN_USB_MANUFACTURER_STRING                    "pd"
#define MAIN_USB_PRODUCT_STRING                         "DAQ v2"
#define MAIN_USB_SERIAL_STRING                          "0000"
#define MAIN_USB_CONFIGURATION_STRING                   "DAQ v2 Config"
#define MAIN_USB_INTERFACE_STRING                       "DAQ v2 Interface"
#define MAIN_USB_DEVICE_VERSION                         0x0100

/* Interrupt priorities */
#define IRQ_UART1_PREEMPT_PRIORITY              2
#define IRQ_UART1_SUB_PRIORITY                  2
#define IRQ_DMA1_STREAM0_PREEMPT_PRIORITY       10
#define IRQ_DMA1_STREAM0_SUB_PRIORITY           10
#define IRQ_OTG_HS_EP1_OUT_PREEMPT_PRIORITY     5
#define IRQ_OTG_HS_EP1_OUT_SUB_PRIORITY         5
#define IRQ_OTG_HS_EP1_IN_PREEMPT_PRIORITY      5
#define IRQ_OTG_HS_EP1_IN_SUB_PRIORITY          5
#define IRQ_OTG_HS_PREEMPT_PRIORITY             5
#define IRQ_OTG_HS_SUB_PRIORITY                 5

/* Pins and ports */
#define DEBUG_1_Pin                             GPIO_PIN_10
#define DEBUG_1_Port                            GPIOE
#define DEBUG_2_Pin                             GPIO_PIN_11
#define DEBUG_2_Port                            GPIOE
#define DEBUG_3_Pin                             GPIO_PIN_12
#define DEBUG_3_Port                            GPIOE
#define DEBUG_4_Pin                             GPIO_PIN_13
#define DEBUG_4_Port                            GPIOE

#define UART1_TX_Pin                            GPIO_PIN_6
#define UART1_TX_Port                           GPIOB
#define UART1_TX_AF                             GPIO_AF7_USART1
#define UART1_RX_Pin                            GPIO_PIN_7
#define UART1_RX_Port                           GPIOB
#define UART1_RX_AF                             GPIO_AF7_USART1

#define SPI3_SCK_Pin                            GPIO_PIN_10
#define SPI3_SCK_Port                           GPIOC
#define SPI3_SCK_AF                             GPIO_AF6_SPI3
#define SPI3_MISO_Pin                           GPIO_PIN_11
#define SPI3_MISO_Port                          GPIOC
#define SPI3_MISO_AF                            GPIO_AF6_SPI3
#define SPI3_MOSI_Pin                           GPIO_PIN_6
#define SPI3_MOSI_Port                          GPIOD
#define SPI3_MOSI_AF                            GPIO_AF5_SPI3

#define BUTTON1_Pin                             GPIO_PIN_2
#define BUTTON1_Port                            GPIOG
#define BUTTON2_Pin                             GPIO_PIN_3
#define BUTTON2_Port                            GPIOG

#define RD_NRESET_Pin                           GPIO_PIN_6
#define RD_NRESET_Port                          GPIOG
#define RD_NCS_Pin                              GPIO_PIN_7
#define RD_NCS_Port                             GPIOG

#define DAC_NLDAC_Pin                           GPIO_PIN_9
#define DAC_NLDAC_Port                          GPIOA
#define DAC_NCS_Pin                             GPIO_PIN_10
#define DAC_NCS_Port                            GPIOA

#define ADC_SPI_NRESET_Pin                      GPIO_PIN_0
#define ADC_SPI_NRESET_Port                     GPIOD
#define ADC_SPI_NCS_Pin                         GPIO_PIN_12
#define ADC_SPI_NCS_Port                        GPIOC

#define SPI2_NSS_Pin                            GPIO_PIN_9
#define SPI2_NSS_Port                           GPIOB
#define SPI2_NSS_AF                             GPIO_AF5_SPI2
#define SPI2_SCK_Pin                            GPIO_PIN_3
#define SPI2_SCK_Port                           GPIOD
#define SPI2_SCK_AF                             GPIO_AF5_SPI2
#define SPI2_MOSI_Pin                           GPIO_PIN_15
#define SPI2_MOSI_Port                          GPIOB
#define SPI2_MOSI_AF                            GPIO_AF5_SPI2

#define USB_OTG_HS_ULPI_STP_Pin                 GPIO_PIN_0
#define USB_OTG_HS_ULPI_STP_Port                GPIOC
#define USB_OTG_HS_ULPI_STP_AF                  GPIO_AF10_OTG2_HS
#define USB_OTG_HS_ULPI_DIR_Pin                 GPIO_PIN_2
#define USB_OTG_HS_ULPI_DIR_Port                GPIOC
#define USB_OTG_HS_ULPI_DIR_AF                  GPIO_AF10_OTG2_HS
#define USB_OTG_HS_ULPI_NXT_Pin                 GPIO_PIN_3
#define USB_OTG_HS_ULPI_NXT_Port                GPIOC
#define USB_OTG_HS_ULPI_NXT_AF                  GPIO_AF10_OTG2_HS
#define USB_OTG_HS_ULPI_CK_Pin                  GPIO_PIN_5
#define USB_OTG_HS_ULPI_CK_Port                 GPIOA
#define USB_OTG_HS_ULPI_CK_AF                   GPIO_AF10_OTG2_HS
#define USB_OTG_HS_ULPI_D0_Pin                  GPIO_PIN_3
#define USB_OTG_HS_ULPI_D0_Port                 GPIOA
#define USB_OTG_HS_ULPI_D0_AF                   GPIO_AF10_OTG2_HS
#define USB_OTG_HS_ULPI_D1_Pin                  GPIO_PIN_0
#define USB_OTG_HS_ULPI_D1_Port                 GPIOB
#define USB_OTG_HS_ULPI_D1_AF                   GPIO_AF10_OTG2_HS
#define USB_OTG_HS_ULPI_D2_Pin                  GPIO_PIN_1
#define USB_OTG_HS_ULPI_D2_Port                 GPIOB
#define USB_OTG_HS_ULPI_D2_AF                   GPIO_AF10_OTG2_HS
#define USB_OTG_HS_ULPI_D3_Pin                  GPIO_PIN_10
#define USB_OTG_HS_ULPI_D3_Port                 GPIOB
#define USB_OTG_HS_ULPI_D3_AF                   GPIO_AF10_OTG2_HS
#define USB_OTG_HS_ULPI_D4_Pin                  GPIO_PIN_11
#define USB_OTG_HS_ULPI_D4_Port                 GPIOB
#define USB_OTG_HS_ULPI_D4_AF                   GPIO_AF10_OTG2_HS
#define USB_OTG_HS_ULPI_D5_Pin                  GPIO_PIN_12
#define USB_OTG_HS_ULPI_D5_Port                 GPIOB
#define USB_OTG_HS_ULPI_D5_AF                   GPIO_AF10_OTG2_HS
#define USB_OTG_HS_ULPI_D6_Pin                  GPIO_PIN_13
#define USB_OTG_HS_ULPI_D6_Port                 GPIOB
#define USB_OTG_HS_ULPI_D6_AF                   GPIO_AF10_OTG2_HS
#define USB_OTG_HS_ULPI_D7_Pin                  GPIO_PIN_5
#define USB_OTG_HS_ULPI_D7_Port                 GPIOB
#define USB_OTG_HS_ULPI_D7_AF                   GPIO_AF10_OTG2_HS

#define I2C4_SCL_Port                           GPIOD
#define I2C4_SCL_Pin                            GPIO_PIN_12
#define I2C4_SCL_AF                             GPIO_AF4_I2C4
#define I2C4_SDA_Port                           GPIOD
#define I2C4_SDA_Pin                            GPIO_PIN_13
#define I2C4_SDA_AF                             GPIO_AF4_I2C4

/* Public macros -------------------------------------------------------------*/
/* Public typedefs -----------------------------------------------------------*/
typedef uint8_t flag_t;
typedef enum
{
	CHANNEL_1 = 0,
	CHANNEL_2 = 1,
	CHANNEL_NONE
} channel_t;
typedef enum
{
	CHANNEL_STATE_1_INPUTCOUPLING_DC_INPUTTYPE_S,
	CHANNEL_STATE_2_INPUTCOUPLING_DC_INPUTTYPE_D,
	CHANNEL_STATE_3_INPUTCOUPLING_AC_INPUTTYPE_S,
	CHANNEL_STATE_4_INPUTCOUPLING_AC_INPUTTYPE_D
} channel_state_t;

/* Public variables ----------------------------------------------------------*/
extern flag_t MAIN_MeasurementRunning;
extern flag_t MAIN_SamplesRequested;

/* Public function prototypes ------------------------------------------------*/
extern void Error_Handler(void);
extern void MAIN_ChangeChannelConfiguration(channel_t channel);

#endif /* __MAIN_H */
